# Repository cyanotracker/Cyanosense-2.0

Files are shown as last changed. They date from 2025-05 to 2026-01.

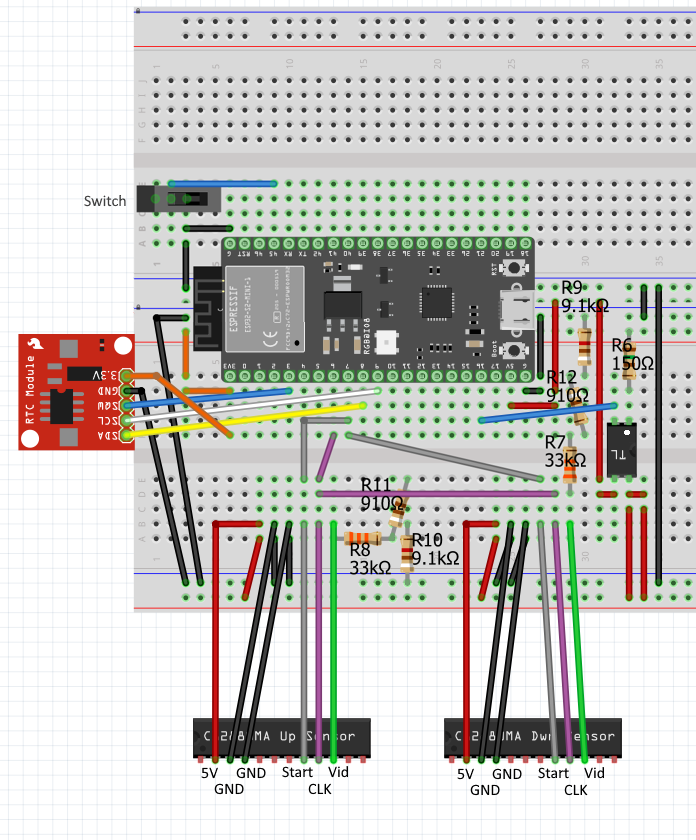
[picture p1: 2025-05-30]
Schematics/Fritizing Diagram Cyanosense 2.0 Offline Verison.png

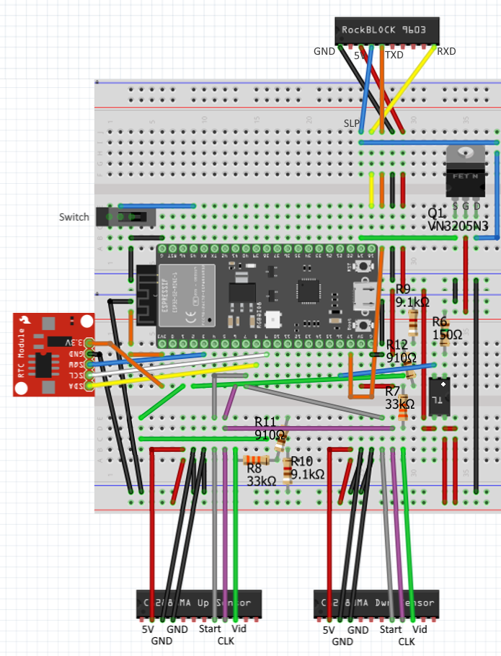
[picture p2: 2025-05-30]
Schematics/Fritizing Diagram Cyanosense 2.0 with Sat Modem.png

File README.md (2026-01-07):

# 🌊 CyanoSense 2.0 (CS2.0) – Low-Cost Hyperspectral System for CyanoHAB Monitoring






**CyanoSense 2.0 (CS2.0)** is a compact, low-cost, open-source spectroradiometer designed to support real-time and offline monitoring of **Cyanobacterial Harmful Algal Blooms (CyanoHABs)** in inland and coastal waters. This repository includes all components needed to **reproduce, assemble, and operate** the CS2.0 device.

> 🛰️ CS2.0 was developed as a complementary in situ validation tool for satellite-based CyanoHAB monitoring.  
> 📝 A scientific publication describing CS2.0 now published. Please cite the work appropriately (see [Citation section](#-citation)) and refer to the paper for broader scientific context and applications.

---

## 📦 What's in This Repository?

This repository includes:

1. 🧩 **3D Printed Parts** – STL files and models for the CS2.0 housing and optical mount components.  
2. 🛠️ **Mechanical Assembly Instructions** – Step-by-step guide with diagrams and instructions for assembling CS2.0.  
3. ⚡ **Electronic Schematics** – Circuit diagrams and wiring layout.  
4. 📷 **Prototype Pictures** – Reference images of a fully built and field-deployed CS2.0 unit.  
5. 💾 **Offline Data Download Instructions** – Guidelines for retrieving stored measurements from the device when internet is not available.  
6. 📂 **Documents Folder** – Contains the **Bill of Materials** (BOM) and **Hamamatsu documentation** including the wavelength space coefficients and sensor specifications.  
   - 📌 An **exhaustive list of all components used** in this project can be found in the Bill of Materials (`Documents/Bill of Materials`).  

🎥 A **tutorial video demonstrating the operation** of CS2.0 is also provided: https://youtu.be/9sZjeJtRidM

---

## 📡 Sensor Details

CS2.0 uses the **Hamamatsu C12880MA** mini-spectrometer to capture hyperspectral light spectra in the range of 380nm - 880nm.

- Records data in **6 channels**, each corresponding to a segment of the full sensor array.  
- Includes calibration code to convert raw intensity values into continuous **wavelength space** using a polynomial mapping.  
- Wavelength mapping is implemented using conversion coefficients provided in the Hamamatsu documentation (see `Documents/`) and handled in the included data extraction code (`/Code/`).  
- Real-time or offline data download is managed through the [CoolTerm](https://freeware.the-meiers.org/) serial terminal tool, described in `/Offline Mode (Download Data off Prototype)/`.

---

## 📚 Usage

To build a CS2.0 prototype and use it for yourself:
- Follow the mechanical and electrical instructions in the `/Mechanical Assembly Instructions/` and `/Schematics/` folders.
- Use `/offline_data/` for accessing data stored during field deployments without real-time upload.

### 🌐 Satellite Data Validation

CS2.0 can be used to **validate satellite-based CyanoHAB products**:
- Overlay CS2.0-derived in situ spectra with coincident satellite-derived reflectance (e.g., Sentinel-2, Landsat, PACE).
- Helps assess model accuracy and algorithm performance under real-world conditions.
- Supports efforts in operational satellite monitoring by offering ground-based reference measurements.

---

## 📄 Citation

- **This sensor and methodology are described in a scientific article, now published open access in *ACS Environmental Science and Technology, Water*.**  
- If you use or build on this work, **please cite the associated article as follows:**<br>
Maniyar, C.B.; Raviprakash, K.; Kumar, A; Seferian, M. A; Firotentino, I and Mishra, D. R. (2025) **Low-Cost System to Support and Expand Cyanobacterial Harmful Algal Bloom Monitoring with New-Generation Ocean Color Satellites.** *ACS Environmental Science and Technology, Water*. DOI: [10.1021/acsestwater.5c00301](https://doi.org/10.1021/acsestwater.5c00301)   
- The article provides a deeper understanding of how CS2.0 fits into the broader **CyanoHAB monitoring paradigm**, including its role in supporting satellite remote sensing efforts.

---

## 🪪 License

- **Code**: [MIT License](LICENSE)
- **Documentation, Schematics, and Hardware Designs**: [Creative Commons Attribution 4.0 International (CC BY 4.0)](https://creativecommons.org/licenses/by/4.0/)

---

## 📬 Contact

For questions, collaborations, or issues, please reach out to:  
**Chintan B. Maniyar** at
📧 [chintanmaniyar@uga.edu] OR [cyanotracker@gmail.com]

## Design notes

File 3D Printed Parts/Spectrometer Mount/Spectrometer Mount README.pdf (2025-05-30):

### Spectrometer Mount

- Allows Spectrometers to be mounted.
- Slips on the Electronics Housing four outer Posts. Requires the Electronics Housing to be modified by trimming the four outer posts by 0.15in (circled in red in Image 2).
- One Spectrometer Mount per sensor. Same mount works for both.
- The Spectrometer Mount should be printed using PETG or similar material

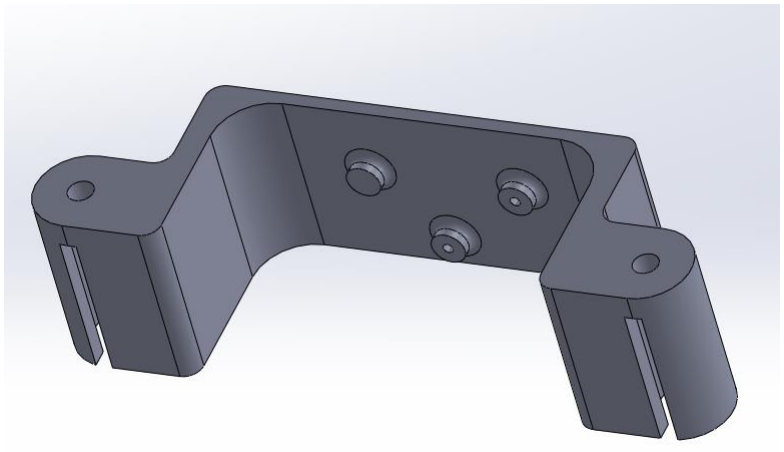
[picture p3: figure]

Image 1

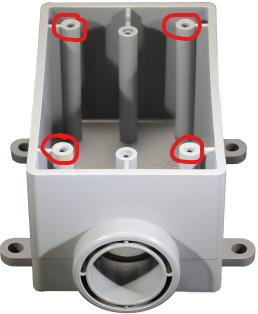
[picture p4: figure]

Image 2

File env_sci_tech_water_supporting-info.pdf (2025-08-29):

Low-cost System to Support CyanoHAB Monitoring with New Generation Ocean Color Satellites: Supporting Information

A GitHub repository containing all designs, schematics, bill of materials and documentation necessary to reproduce and replicate Cyanosense2.0 sensor can be found here: https://github.com/cyanotracker/Cyanosense-2.0

A video demonstrating operation of Cyanosense2.0 can be found here: https://youtu.be/9sZjeJtRidM

A. CyanoHAB Models and Indices; and Uncertainty Metrics

NDCI =

Rrs(708)−Rrs(665)
Rrs(708)+Rrs(665)

(1)

PC3 = (Rrs

−1
(620) − Rrs

−1
(665)) × Rrs(708) | (2)

CI = −1 × { Rrs(681) − Rrs(665) − (Rrs(708) − Rrs(665)) ×

681−665
708−665
} | (3)

PCI = Rrs(560) − Rrs(620) + (Rrs(665) − Rrs(560)) ×

620−560
665−560

(4)

where Rrs(560) and corresponds to OLCI's band-6; Rrs(620) corresponds to OLCI's band-7; Rrs(665) corresponds to OLCI's band-8; Rrs(681) corresponds to OLCI's band-10; Rrs(708) corresponds to OLCI's band-11. These bands are available on PACE OCI verbatim.

A.1 Uncertainty Metrics for Model Validation and Spectral Magnitude Evaluation

%NRMSE = √∑
(pi−pi

′
)

2
n

n
i=1 | ×

1

pmax−pmin

× 100% | (5)

MAPE =

1
n

∑

|pi−pi

′
pi

n
i=1 | × 100% | (6)

β = 100 × sgn (median (loge (
pi

′

pi

))) × (e

|median(loge(
pi

′

pi

))|
| | − 1) (7)

where p is the reference value (SVC-HR); p' is the measured value (CS2.0); n is the total number of samples.

A.2 Uncertainty Metrics for Spectral Shape Evaluation

SAM = cos

−1 (
RrsCS2.0⋅RrsSVC
||RrsCS2.0|| ||RrsSVC||
) | (8)

SID(p, q) = Σi pi

′
log(

pi

′

pi

) + pi

log(

pi

′

pi

) | (9)

SED = √∑ | (RrsCS2.0 − RrsSVC)
N | 2
i=1

(10)

where p is the reference value (SVC-HR); p' is the measured value (CS2.0); N is the total number of wavenumbers (wavelength).

B. Calibration Coefficients for Lw, Lc and Lsky

The Hamamatsu C12880MA spectrometer records data in a 6-channel pixel space, which is converted to wavelength space using coefficients provided by the manufacturer as found in this document. (https://github.com/cyanotracker/Cyanosense-2.0/blob/main/Documents/Sensor%20Calibration%20Data.pdf) Once in wavelength space, the data is still in Arbitrary Units (AU), representing Intensity. To convert this intensity into various radiances (Lw, Lc and Lsky); we provide a wavelength-dependent set of coefficients and biases below for each component for the wavelength range 390nm – 880nm. This table can be found at the end of this document due to its length. Figure 1 shows the Rrs spectra from CS2.0 overlaid with coincident Rrs spectra from SVC-HR, following leave-one location out cross-validation, for all stations across the 6 study sites (lakes).

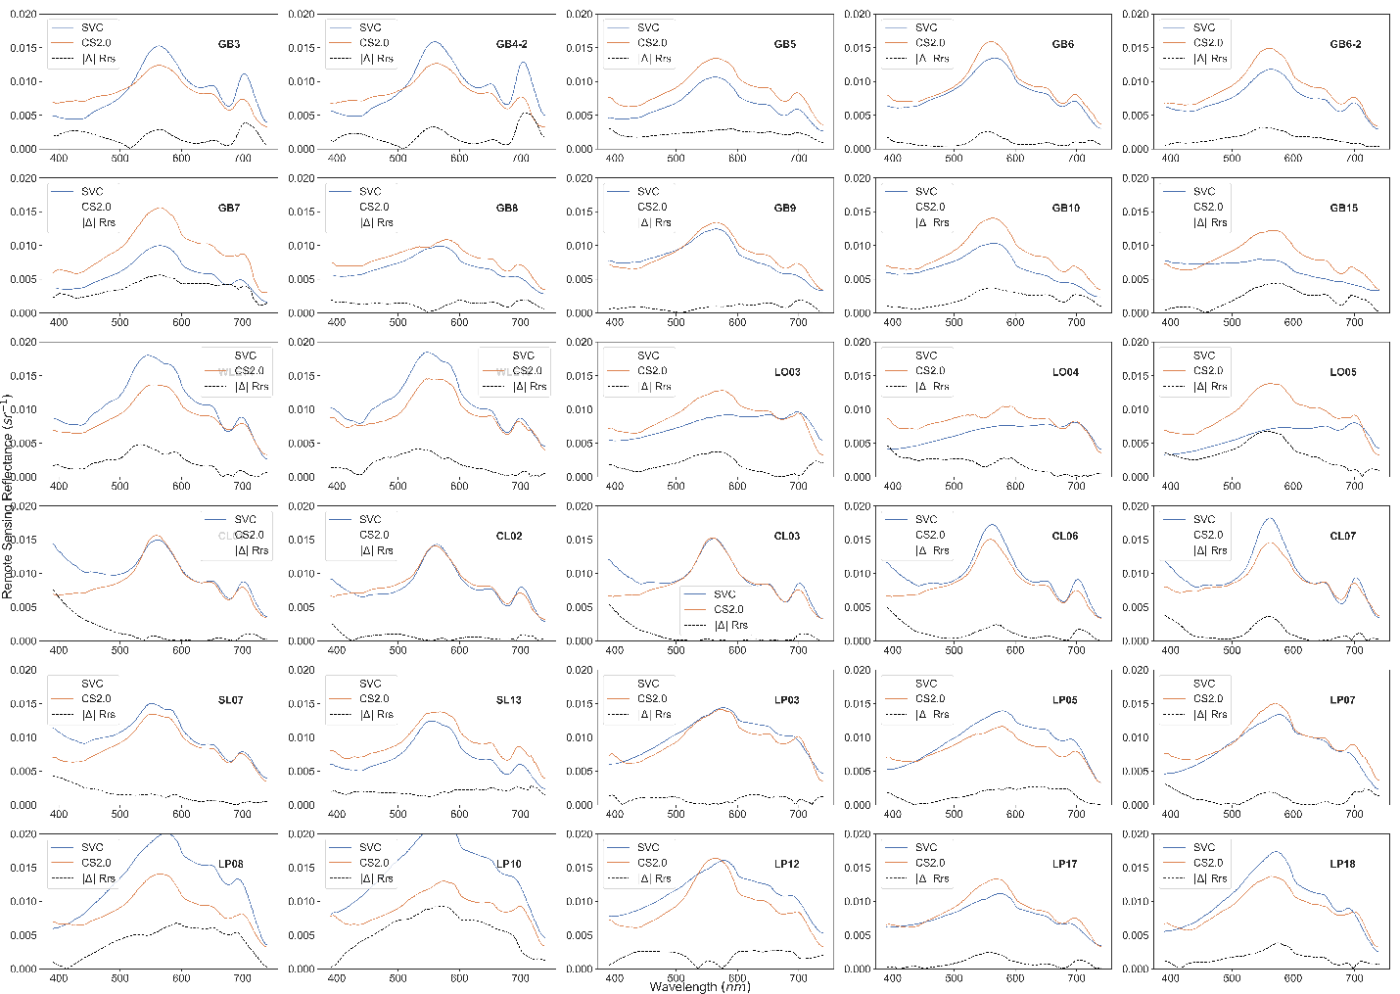
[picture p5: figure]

Figure 1: In-situ Rrs spectra of CS2.0 and SVC overlayed onto each other for all sampling stations. Dotted line represents absolute error in Rrs for CS2.0 spectra with SVC spectra as reference.

C. Upscaling CS2.0 to Satellite Spectral Configuration: Radiometric Evaluation

Table 1: A summary of evaluation metrics for - (Top half): CyanoHAB specific bands in PACE (OCI) as well as Sentinel-3 (OLCI). Satellite Rrs simulated from CS2.0 is evaluated against satellite Rrs simulated from SVC-HR; and (Bottom half): CyanoHAB indices/models applied on PACE (OCI) as well as Sentinel-3 (OLCI). Satellite indices/models simulated from CS2.0 are evaluated against the corresponding ones simulated from SVC-HR.

%NRMSE and MAPE | R
| | | | 2 | Band Usage
| PACE (OCI) | Sentinel-3 (OLCI) | PACE (OCI) | Sentinel-3 (OLCI)
CyanoHAB Specific Bands
560 nm | 23.98% & 22.97% | 24.00% & 22.80% | 0.45 | 0.34 | PCI
620 nm | 21.62% & 20.33% | 21.63% & 20.33% | 0.41 | 0.40 | PC3, PCI
665 nm | 20.73% & 19.39% | 20.88% & 19.51% | 0.55 | 0.51 | NDCI, PC3, CI, PCI
681 nm | 19.92% & 18.34% | 19.83% & 18.34% | 0.58 | 0.61 | CI
708 nm | 22.6% & 24.19% | 22.66% & 24.19% | 0.32 | 0.38 | NDCI, PC3, PCI
CyanoHAB Specific Spectral Indices/Models
NDCI | 16.24% | 16.86% | 0.77 | 0.74 | -
PC3 | 16.51% | 16.64% | 0.77 | 0.75 | -
CI | 13.96% | 14.28% | 0.83 | 0.83 | -
PCI | 15.17% | 18.28% | 0.83 | 0.79s | -

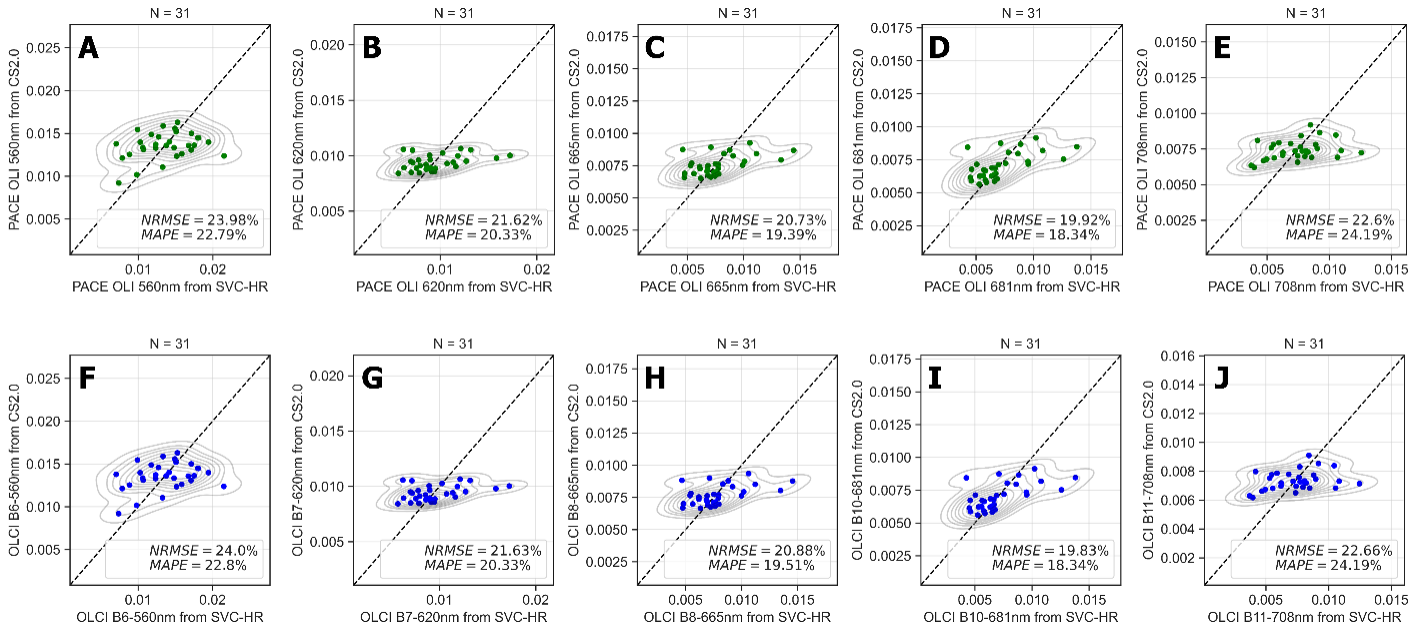
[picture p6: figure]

Figure 2: Top row (A-E): Validation of PACE {CS2.0} simulated Rrs with PACE {SVC-HR} simulated Rrs as reference (shown in green). Bottom row (F-J): Validation of OLCI {CS2.0} simulated Rrs with OLCI {SVC-HR} simulated Rrs as reference (shown in blue). Dotted line is the reference (1:1) line.

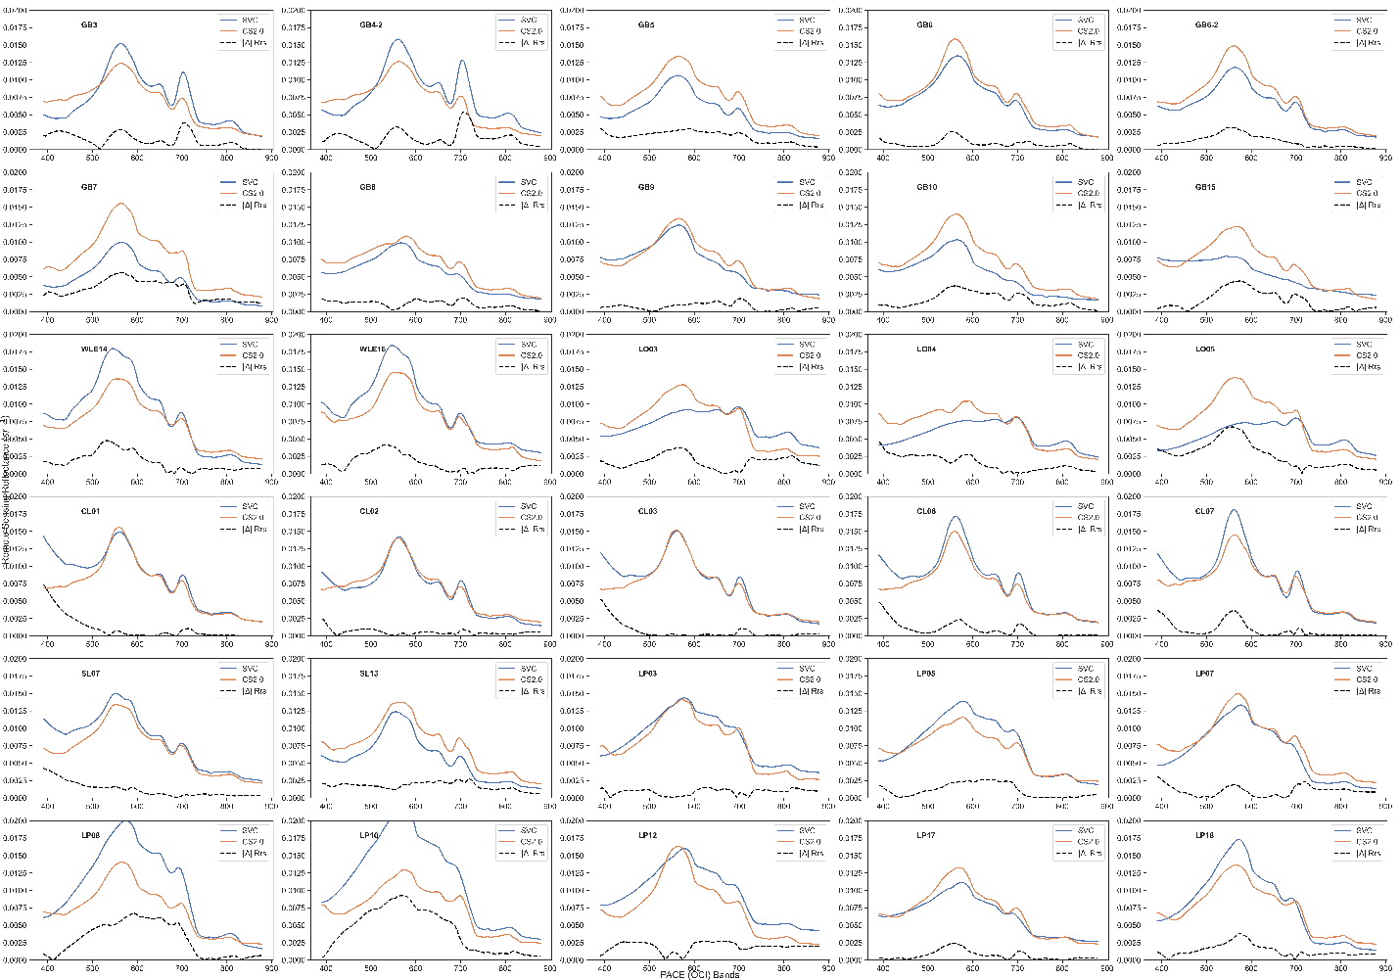
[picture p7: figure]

Figure 3: PACsE (OCI) spectral shape derived from PACECS2.0 Rrs (in orange) overlayed onto the corresponding spectral shape derived from PACESVC-HR Rrs (in blue) for all sampling stations. Dotted line is the relative error.

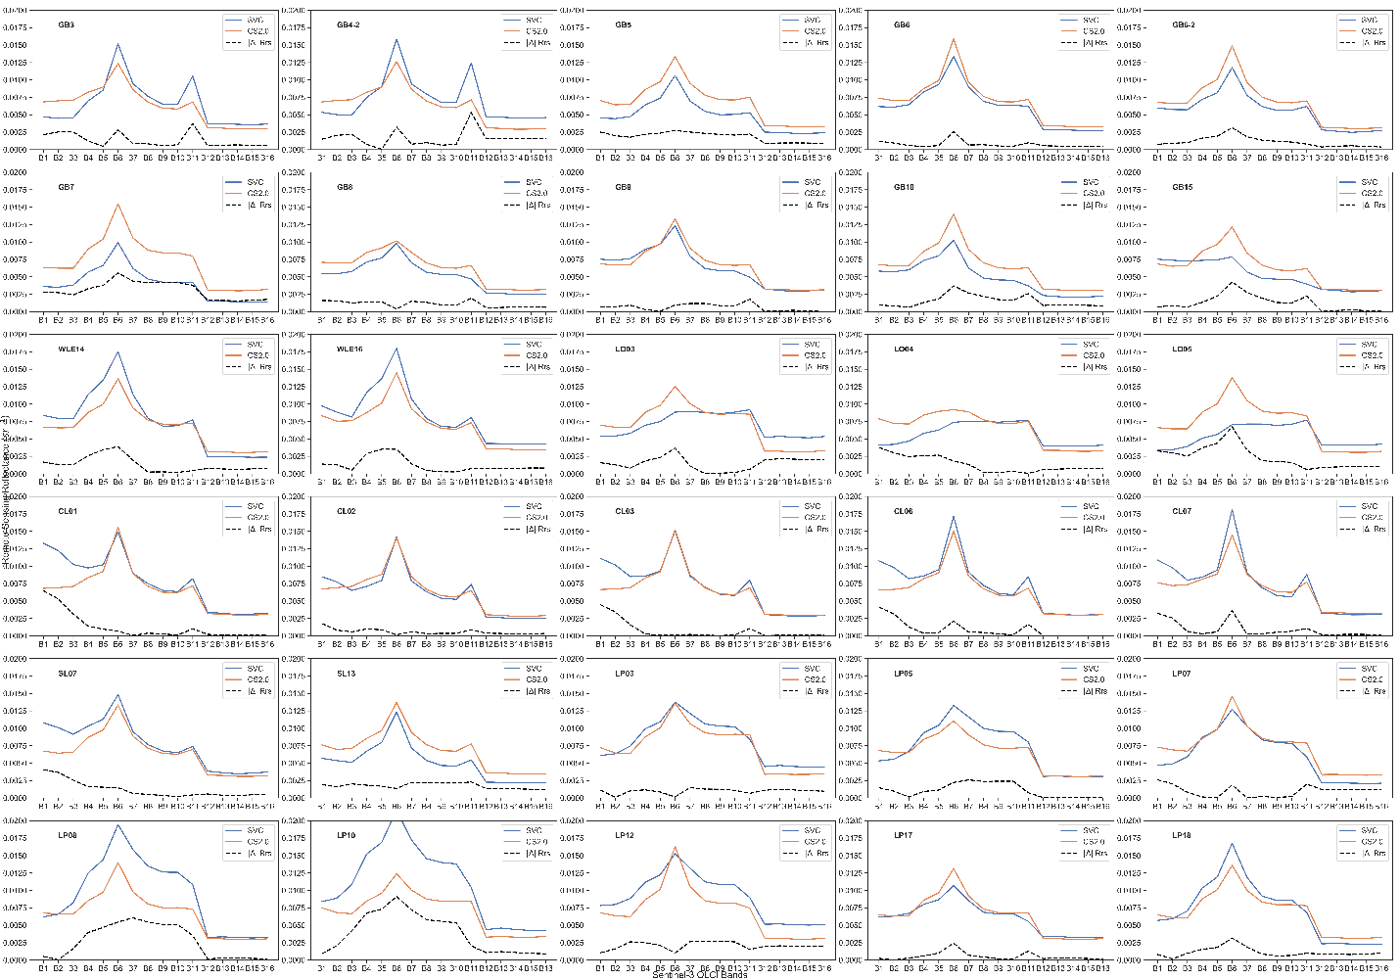
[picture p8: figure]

Figure 4: Sentinel-3 (OLCI) spectral shape derived from Sentinel-3CS2.0 Rrs (in orange) overlayed onto the corresponding spectral shape derived from Sentinel-3SVC-HR Rrs (in blue) for all sampling stations. Dotted line is the relative error.

D. List and Price of Components

Table 2 includes a comprehensive list of all the components used in the development of CS2.0, along with their price listings. This table also serves as a budget table for CS2.0. Each component name carries the hyperlink to its online listing that was used to make the purchase at the time of sensor development. Note that the prices are based on the EXACT number to build the prototype, unless noted otherwise. Tax and any shipping costs are NOT included. The total cost to build CS2.0 was $1,300.33.

Table 2: A comprehensive list of all components used in the development of CS2.0 with their price listings

Component | Quantity | Price | Purpose

Electronic Parts

Hamamatsu C12880MA Micro (https://www.digikey.com/en/products/detail/groupgets-llc/BO-HAMA-C12880-V2-SENSOR/14306449) | 2 ($350 each) | $700 | Spectrometers for CS2.0
Spectrometer (https://www.digikey.com/en/products/detail/groupgets-llc/BO-HAMA-C12880-V2-SENSOR/14306449)
TLP3556A Photorelay (https://www.mouser.com/ProductDetail/Toshiba/TLP3556ATP1F?qs=r5DSvlrkXmJCPc02EG%252Bwtw%3D%3D) | 1 | $4.20 | Turns sensors on and off
RockBlock 9603 Iridium (https://www.adafruit.com/product/4521) | 1 | $299.95 | Satellite data transmission for
Satellite Modem (https://www.adafruit.com/product/4521) | | | CS2.0
RockBlock 9603 Accessory (https://www.adafruit.com/product/4529) | 1 | $4.95 | Adapter cable to ESP32 interface
Cable (https://www.adafruit.com/product/4529)
M1600HCT-P-SMA Iridium (https://www.sparkfun.com/products/16838) | 1 | $64.95 | Antenna for Iridium modem
Passive Antenna (https://www.sparkfun.com/products/16838)
SMA Male with Waterproof (https://www.amazon.com/dp/B082964WZ3?psc=1&ref=ppx_yo2ov_dt_b_product_details) | 1 | $3.63 | Antenna cable for Iridium
Ring & Bulkhead Antenna with (https://www.amazon.com/dp/B082964WZ3?psc=1&ref=ppx_yo2ov_dt_b_product_details) | | | modem
Cable (https://www.amazon.com/dp/B082964WZ3?psc=1&ref=ppx_yo2ov_dt_b_product_details)
ESP32-S2 Saola Dev Kit (https://www.adafruit.com/product/4693) | 1 | $14.50 | Microcontroller for the system
DS3231 Real Time Clock (https://www.amazon.com/DS3231-Precision-AT24C32-Arduino-Raspberry/dp/B07V68443F/ref%3Dsr_1_1_sspa) | 1 | $3.80 | RTC to control wake-up and
| | | sleep for ESP32
DIYHZ 1P2T SPFT Vertical (https://www.amazon.com/dp/B07BD1SPYG?psc=1&ref=ppx_yo2ov_dt_b_product_details) | 1 | $0.09 | Slide switch to toggle ESP32
Slide Switch (https://www.amazon.com/dp/B07BD1SPYG?psc=1&ref=ppx_yo2ov_dt_b_product_details) | | | between manual and
| | | autonomous mode
Voltaic 2W Solar Charger Kit (https://voltaicsystems.com/2-watt-kit/) | 1 | $5.99 | Solar panel and battery
USB to Micro USB Cable (https://www.amazon.com/dp/B07CKXQ9NB?ref=ppx_yo2ov_dt_b_product_details&th=1) | 1 | $4.99 | Connects ESP32 to battery
SchmalzTech Breadboard (https://www.amazon.com/dp/B0B1XGCFGW?psc=1&ref=ppx_yo2ov_dt_b_product_details) | 2 ($8.99 each) | $17.98 | Breadboard for system
ST-BB-470 (https://www.amazon.com/dp/B0B1XGCFGW?psc=1&ref=ppx_yo2ov_dt_b_product_details)
Jumper Wire Kit (https://www.amazon.com/AUSTOR-Lengths-Assorted-Preformed-Breadboard/dp/B07CJYSL2T/ref%3Dsr_1_4) | 1 | $11.99 | Wiresfor breadboard
10 cm Jumper Wires Assorted (https://www.amazon.com/dp/B07GD1XFWV?ref=ppx_yo2ov_dt_b_product_details&th=1) | 1 | $6.98 | Jumper wires for RTC
Kit (https://www.amazon.com/dp/B07GD1XFWV?ref=ppx_yo2ov_dt_b_product_details&th=1)
40 cm Jumper Wires Assorted (https://www.amazon.com/dp/B07GD1TH2K?ref=ppx_yo2ov_dt_b_product_details&th=1) | 1 | $11.99 | Jumper wires for spectrometers
Kit (https://www.amazon.com/dp/B07GD1TH2K?ref=ppx_yo2ov_dt_b_product_details&th=1)

Mechanical Parts

Waterproof Electrical Junction (https://www.amazon.com/dp/B0B87VR84G?ref=ppx_yo2ov_dt_b_product_details&th=1) | 1 | $19.99 | Electronics housing
Box IP67 (https://www.amazon.com/dp/B0B87VR84G?ref=ppx_yo2ov_dt_b_product_details&th=1)
PVC 1-Gang Type FSE Box (https://www.lowes.com/pd/Kraloy-PVC-3-4-in-FSE-Single-Gang-Box-91-Hub-93/5001212811) | 1 | $7.68 | Sensor housing
TayMac 1-Gang Weatherproof (https://www.lowes.com/pd/TayMac-1-Gang-Rectangle-Plastic-Weatherproof-Electrical-Box-Cover/5004945479) | 1 | $3.58 | Cover for sensor housing
Box Cover (https://www.lowes.com/pd/TayMac-1-Gang-Rectangle-Plastic-Weatherproof-Electrical-Box-Cover/5004945479)
10 ft Schedule 40 PVC Conduit (https://www.lowes.com/pd/CANTEX-Common-3-4-in-Actual-75-In-Non-Metallic-Pvc-10-ft-Conduit/3568512) | 1 | $2.06 | To connect sensor and electronic
| | | housings. Cut to 2 ft.
Schedule 40 PVC Bushing (https://www.lowes.com/pd/CANTEX-3-4-in-Bushing-Connector-Schedule-40-PVC-Compatible-Schedule-80-PVC-Compatible-Conduit-Fitting/1000321591) | 1 | $0.60 | Attaches PVC pipe to electronics
Connector Conduit Fitting (https://www.lowes.com/pd/CANTEX-3-4-in-Bushing-Connector-Schedule-40-PVC-Compatible-Schedule-80-PVC-Compatible-Conduit-Fitting/1000321591) | | | housing
3/4-in Zinc-plated Steel Conduit (https://www.lowes.com/pd/Sigma-Electric-ProConnex-3-4-in-Conduit-Locknut-Intermediate-Metal-Conduit-Compatible-Galvanized-Rigid-Conduit-Compatible-Rigid-Metal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) | 1 | $0.39 | Screws the bushing connector to
Locknut (https://www.lowes.com/pd/Sigma-Electric-ProConnex-3-4-in-Conduit-Locknut-Intermediate-Metal-Conduit-Compatible-Galvanized-Rigid-Conduit-Compatible-Rigid-Metal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) | | | the electronics housing

1-in Zinc-plated Standard Flat (https://www.lowes.com/pd/Hillman-1-Count-x-2-in-Zinc-Plated-Standard-SAE-Flat-Washer/3006230) | 1 | $0.78 | Adds support to the inside of the
Washer (https://www.lowes.com/pd/Hillman-1-Count-x-2-in-Zinc-Plated-Standard-SAE-Flat-Washer/3006230) | electronics housing to prevent
flex
1/2-inch Oversize Union Washer (https://www.amazon.com/dp/B09TPGN29W?psc=1&ref=ppx_yo2ov_dt_b_product_details) | 1 | $0.30 | Waterproofs the electronics box
Flat Plumbing Slip Joint Washer (https://www.amazon.com/dp/B09TPGN29W?psc=1&ref=ppx_yo2ov_dt_b_product_details) | to pipe connection
Rubber (https://www.amazon.com/dp/B09TPGN29W?psc=1&ref=ppx_yo2ov_dt_b_product_details)
3x30mm Round Aluminum (https://www.amazon.com/dp/B01MYBB70W?ref=ppx_yo2ov_dt_b_product_details&th=1) | 4 | $4.60 | Standoff to support top layer in
Column Standoffs (https://www.amazon.com/dp/B01MYBB70W?ref=ppx_yo2ov_dt_b_product_details&th=1) | electronics box
3x16mm Thumb Screws (https://www.amazon.com/dp/B01MSLME5A?psc=1&ref=ppx_yo2ov_dt_b_product_details) | 4 | $5.20 | To screw down top layer
4/40 Hex Machine Nuts (https://www.amazon.com/Hillman-140009-Machine-Screw-Piece/dp/B001B2QP3C/ref%3Dsr_1_3?s=industrial) | 4 | $0.24 | Nuts to screw solar panel
M3x Screws (https://www.amazon.com/uxcell-M3x10mm-Phillips-Stainless-Fasteners/dp/B07MF2ZTBG/ref%3Dsxin_16_pa_sp_search_thematic_sspa?cv_ct_cx=m3x10%2Bmachine%2Bscrews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) | 4 | $0.94 | Screws standoffs to mounting
plate in electronics housing
Microscope Cover Glass Slips (https://www.amazon.com/dp/B095N8DNY1?psc=1&ref=ppx_yo2ov_dt_b_product_details) | 2 | $8.99 (not | Cover glass were used as the
exact) | lens for spectrometer housing
GE Advanced Silicone (https://www.amazon.com/GE-GE500-Silicone-Window-Squeeze/dp/B000M2UPAG/ref%3Dsr_1_17) | 1 | $14.99 (not | To seal solar panel and cable for
exact) | waterproofing; to attach glass
lens in sensor housing
Miscellaneous* | 1 | $20 (not | TPU material used for 3D
exact) | printed FOV adapter, PETG
material, other 3D printed parts and foam pads used for battery
Total Cost | $1,300.33

*Gray card (external to the CS2.0 system) for radiometric calibration of the spectrometer can be obtained at a nominal price of $5: https://a.co/d/i3NDbEW

E. Heatproof Testing on Field

To test the heatproof design of the sensor and electronics housing, CS2.0 was deployed in autonomous mode for a week at Lake Herrick in Athens, Georgia. Ambient temperature and temperature inside the electronics and sensor housing box was recorded every half an hour. Tables 3 and 4 show the temperature variation from the most sunny and the most cloudy days of the week.

Table 3: Temperature Data from 3/31/23 (Red Textshows highest Box Temp)

Time | Box ◦C | Ambient ◦C | Outside Conditions
10:30 am | 24.0 | 18.9 | Cloudy
11:00 am | 25.2 | 19.5 | Cloudy
11:30 am | 26.9 | 20.9 | Cloudy
12:00 pm | 29.8 | 22.2 | Partially Sunny
12:30 pm | 31.5 | 23.0 | Partially Sunny
01:00 pm | 32.6 | 23.7 | Partially Sunny
01:30 pm | 30.1 | 24.4 | Cloudy
02:00 pm | 31.5 | 24.6 | Partially Sunny
02:30 pm | 32.1 | 24.8 | Partially Sunny
03:00 pm | 28.9 | 24.3 | Cloudy
03:30 pm | 26.4 | 24.0 | Cloudy
04:00 pm | 32.1 | 23.9 | Partially Sunny
04:30 pm | 27.1 | 23.5 | Cloudy
05:00 pm | 31.5 | 23.2 | Partially Sunny
05:30 pm | 29.0 | 23.0 | Cloudy
06:00 pm | 27.0 | 22.7 | Cloudy

Table 4: Temperature Data from 4/1/23 (Red Text shows highest Box Temp)

Time | Box ◦C | Ambient ◦C | Outside Conditions
01:00 pm | 36.3 | 22.2 | Sunny
01:30 pm | 38.6 | 22.9 | Sunny
02:00 pm | 39.4 | 25.4 | Sunny
02:30 pm | 38.8 | 26.3 | Sunny
03:00 pm | 39.1 | 26.2 | Sunny
03:30 pm | 39.3 | 26.5 | Sunny
04:00 pm | 39.2 | 26.8 | Sunny
04:30 pm | 38.3 | 26.6 | Sunny
05:00 pm | 33.3 | 25.0 | Sunny
05:30 pm | 29.0 | 23.0 | Cloudy
06:00 pm | 27.0 | 22.7 | Cloudy
F. Power Budget from Field Operation

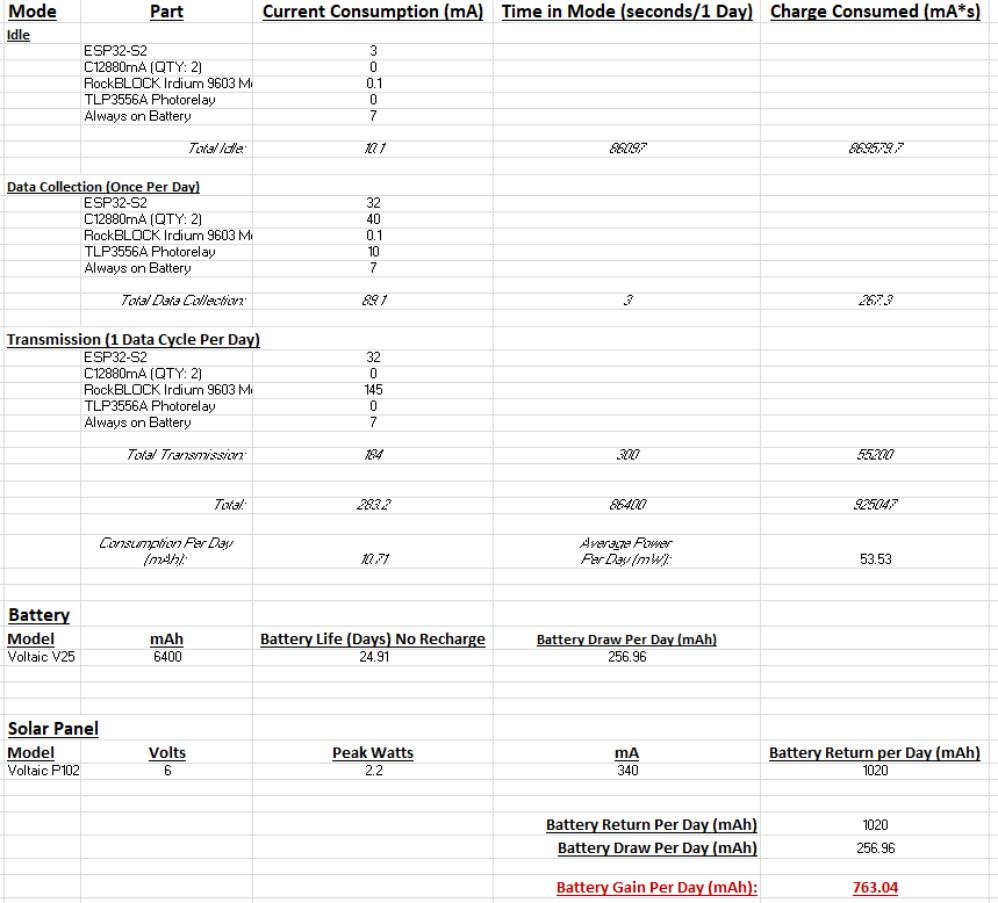
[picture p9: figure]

Figure 2: Actual power budget recorded after field-deployment of CS2.0

Table 2: Calibration coefficients to convert CS2.0 AU to Radiance (390nm – 880nm)

Wavelength | Lw | Lc | Lsky
Coefficient | Bias | Coefficient | Bias | Coefficient | Bias
390 | -0.377420664 | 6232.905 | 13.05778056 | 116470 | 3.007927386 | 43970.94
391 | -0.31822665 | 5671.419 | 11.58347595 | 107223.1 | 2.659524231 | 40136.66
392 | -0.283673801 | 5447.732 | 10.97939188 | 104127.6 | 2.527039034 | 38673.75
393 | -0.252053223 | 5228.914 | 10.40399777 | 101064.3 | 2.399893116 | 37209.26
394 | -0.20133233 | 5080.749 | 9.820725814 | 100274.6 | 2.224268735 | 36576.97
395 | -0.171353458 | 5196.92 | 9.739188789 | 104370.7 | 2.189416713 | 37962.29
396 | -0.164189121 | 5373.281 | 9.858000178 | 108557.6 | 2.232114083 | 39152.24
397 | -0.166732543 | 5999.62 | 10.81811365 | 123296.9 | 2.465840795 | 43535.29
398 | -0.169384947 | 6590.819 | 11.48004436 | 137701 | 2.658099038 | 47812.75
399 | -0.181796642 | 7227.734 | 12.10525959 | 152174.5 | 2.873149956 | 51749.96
400 | -0.192090515 | 8036.909 | 12.4003705 | 175655.9 | 3.131415331 | 56862.43
401 | -0.222795853 | 8283.76 | 12.41530014 | 179658.6 | 3.197529273 | 57193.25
402 | -0.251521545 | 8526.865 | 12.30716215 | 184576.2 | 3.260941638 | 57527.1
403 | -0.269243666 | 8608.086 | 11.88870645 | 187942.1 | 3.262473675 | 56635.39
404 | -0.286053748 | 8617.279 | 11.66481333 | 187241.1 | 3.245135617 | 55592.96
405 | -0.300460512 | 8618.181 | 11.36599549 | 187125.8 | 3.225967583 | 54561.39
406 | -0.306311257 | 8623.513 | 11.14471053 | 189422.6 | 3.242026289 | 53529.41
407 | -0.318471205 | 8795.883 | 11.11447854 | 194319.4 | 3.322266214 | 53170.01
408 | -0.334832259 | 8948.358 | 10.70657061 | 199365 | 3.378428783 | 52764.01
409 | -0.353354029 | 9094.713 | 10.53986723 | 202886.8 | 3.447308776 | 52466.27
410 | -0.363952303 | 9312.512 | 10.37199412 | 210647.1 | 3.555777653 | 52619.75
411 | -0.380574994 | 9509.185 | 10.07485453 | 217455.6 | 3.645712163 | 52696.69
412 | -0.411278136 | 9767.2 | 9.564034891 | 226160.6 | 3.744305954 | 52785.21
413 | -0.42896204 | 9928.667 | 8.764538428 | 236511.5 | 3.822303668 | 52355.29
414 | -0.448300993 | 10035.2 | 8.616180935 | 238928.4 | 3.86887533 | 51966.55
415 | -0.466471134 | 10136.64 | 8.460274949 | 241408.4 | 3.915055861 | 51580.45
416 | -0.470185205 | 10110.08 | 8.235706463 | 242072.7 | 3.922329896 | 50492.66
417 | -0.486716481 | 10134.48 | 8.071849322 | 241899.8 | 3.924576815 | 49881.57
418 | -0.502227969 | 10153.58 | 7.91077645 | 241703.4 | 3.925525397 | 49277.58
419 | -0.510918898 | 10225.86 | 7.894340963 | 244660.1 | 3.974104264 | 48862
420 | -0.537795881 | 10326.13 | 7.980960953 | 244842.3 | 4.029193663 | 48530.23
421 | -0.563588116 | 10419.35 | 8.050386137 | 245160.7 | 4.081113403 | 48222.09
422 | -0.572163781 | 10410.38 | 8.314467521 | 243910.7 | 4.103872234 | 47588.02
423 | -0.577193174 | 10324.52 | 8.460137732 | 239919.9 | 4.078685852 | 46587.9
424 | -0.599367043 | 10393.12 | 8.594059284 | 238817.6 | 4.091664849 | 46433.58
425 | -0.626876918 | 10466.84 | 8.98596203 | 235843.4 | 4.082342477 | 46544.27
426 | -0.631175062 | 10332.04 | 9.163530475 | 230655.8 | 4.000051568 | 45761.32
427 | -0.619617344 | 10081.7 | 9.005153828 | 224372.8 | 3.894867082 | 44460.92
428 | -0.606648042 | 9825.928 | 8.835191946 | 218178.2 | 3.788672614 | 43158.21

429 | -0.561038858 | 9215.235 | 8.506050111 | 205399.7 | 3.590927477 | 40237.13
430 | -0.570113136 | 9304.418 | 8.702257652 | 207105.9 | 3.659329187 | 40289.07
431 | -0.578240853 | 9389.436 | 8.898709286 | 208813.3 | 3.727699605 | 40346.45
432 | -0.587022747 | 9966.783 | 9.569912015 | 225863 | 4.033819808 | 42754.19
433 | -0.59099272 | 10197.47 | 9.730694667 | 232794.4 | 4.122820593 | 43682.35
434 | -0.594764439 | 10427.5 | 9.876147436 | 239839.5 | 4.211336079 | 44611.27
435 | -0.589153659 | 10685.71 | 10.04438109 | 249348 | 4.343050994 | 45501.61
436 | -0.571118906 | 10709.44 | 9.894504736 | 253717.8 | 4.386117311 | 45280.43
437 | -0.557233199 | 10609.4 | 9.771882112 | 252965.8 | 4.372413169 | 44725.45
438 | -0.542923125 | 10507.64 | 9.647375746 | 252227.2 | 4.358105065 | 44172.77
439 | -0.522400982 | 10510.58 | 9.788509669 | 255020.1 | 4.409910718 | 43943.34
440 | -0.521749439 | 10712.29 | 10.01203249 | 260974.7 | 4.492541929 | 44637.78
441 | -0.520927516 | 10913.26 | 10.23126292 | 266958.7 | 4.574952564 | 45333.07
442 | -0.51949674 | 11266.2 | 10.58432657 | 277186.3 | 4.718470005 | 46382.61
443 | -0.504414425 | 11280.27 | 10.20394428 | 281081.2 | 4.749829451 | 45985.33
444 | -0.488855282 | 11290.68 | 9.729485186 | 285712.5 | 4.78017559 | 45591.19
445 | -0.478545415 | 11368.66 | 9.70159223 | 288072.4 | 4.810839507 | 45212.83
446 | -0.4740744 | 11567.84 | 9.765876819 | 293293 | 4.891614618 | 45240.53
447 | -0.474438534 | 11779.02 | 9.848005054 | 299231.4 | 4.988401611 | 45669.76
448 | -0.471310601 | 11984.28 | 10.11585203 | 303570 | 5.058368711 | 46181.09
449 | -0.473061576 | 12343.07 | 10.38235522 | 311328.8 | 5.156335673 | 46811.51
450 | -0.465405798 | 12363.08 | 10.26797501 | 312393.1 | 5.164262001 | 46468.2
451 | -0.457252401 | 12380.52 | 10.14650531 | 313514.1 | 5.171954069 | 46125.97
452 | -0.440936068 | 12230.3 | 9.834662824 | 309820.6 | 5.086057474 | 44737.08
453 | -0.425942747 | 12167.74 | 9.700054265 | 309697.4 | 5.071925859 | 44301.09
454 | -0.410470641 | 12102.57 | 9.555039623 | 309656.1 | 5.057244874 | 43867.17
455 | -0.401351345 | 12327.04 | 9.623289802 | 316461.5 | 5.126780786 | 44003.66
456 | -0.385781828 | 12421 | 9.516204039 | 320779.7 | 5.145006571 | 43770.67
457 | -0.370448274 | 12381.98 | 9.312389063 | 321981.8 | 5.126986026 | 43388.25
458 | -0.355924119 | 12342.27 | 8.405580509 | 328947.4 | 5.137472448 | 42960.52
459 | -0.333581403 | 12343.01 | 7.457138923 | 338435.7 | 5.166304464 | 42460.62
460 | -0.321370479 | 12385.49 | 7.463701484 | 340866.3 | 5.177313335 | 42446.02
461 | -0.309182285 | 12427.37 | 7.457393277 | 343398.4 | 5.187963512 | 42432.9
462 | -0.286745006 | 12414.32 | 7.32763906 | 345810.5 | 5.169054216 | 42062.86
463 | -0.264907712 | 12291.53 | 7.251180198 | 344374.4 | 5.156636772 | 41308.19
464 | -0.242968012 | 12165.56 | 7.136884076 | 343240.3 | 5.142706396 | 40561.36
465 | -0.20987202 | 11905.74 | 7.018596703 | 339121.3 | 5.057779797 | 39364.72
466 | -0.181193955 | 11814.91 | 6.97083856 | 339549.6 | 5.033344198 | 38748.23
467 | -0.163442148 | 11742.6 | 6.824896759 | 339959.3 | 5.011830765 | 38387.17
468 | -0.140803081 | 11646.7 | 7.344805372 | 334995.3 | 4.998361506 | 37959.97
469 | -0.107590211 | 11572.15 | 7.92239053 | 331292.3 | 4.998059578 | 37449.57
470 | -0.084087516 | 11517.89 | 7.43942168 | 336310.2 | 5.015254389 | 37099.19
471 | -0.060640716 | 11461.33 | 6.824216369 | 342389.4 | 5.031304863 | 36753.31

472 | -0.0228028 | 11491.04 | 6.091305265 | 354531.4 | 5.091619996 | 36636.79
473 | 0.006325624 | 11377.26 | 6.404839267 | 352469.3 | 5.079065431 | 36294.27
474 | 0.0345321 | 11264.13 | 6.697515886 | 350561 | 5.064285541 | 35963.63
475 | 0.076608948 | 11101.56 | 5.699205033 | 359807.2 | 5.073742596 | 35308.75
476 | 0.120821996 | 10951.89 | 4.638147091 | 370443.4 | 5.106740199 | 34704.59
477 | 0.14685629 | 10891.21 | 3.494225006 | 381856.8 | 5.157457286 | 34425.86
478 | 0.166992877 | 10865.06 | 3.508715726 | 383930.9 | 5.193029803 | 34364.77
479 | 0.202498785 | 10802.74 | 3.387744969 | 387452.3 | 5.234968415 | 34160.77
480 | 0.224811677 | 10722.66 | 2.91331937 | 391760.7 | 5.243884077 | 34017.85
481 | 0.247264153 | 10641.49 | 2.434882702 | 396099.3 | 5.25265415 | 33875.82
482 | 0.281310916 | 10413.83 | 1.750260883 | 398328.8 | 5.198504097 | 33238.26
483 | 0.296318261 | 9932.445 | 1.238442726 | 386430.9 | 4.978863106 | 31706.02
484 | 0.303626211 | 9679.36 | 1.199278887 | 378508.5 | 4.871900901 | 30924.85
485 | 0.310483961 | 9423.961 | 2.061821542 | 363316.3 | 4.761384527 | 30100.72
486 | 0.326085331 | 9243.837 | 3.19144789 | 349661.6 | 4.69514689 | 29256.95
487 | 0.345323408 | 9344.968 | 2.523732382 | 361599.9 | 4.759563082 | 29574.61
488 | 0.364924721 | 9443.717 | 1.817634055 | 373838.6 | 4.823515938 | 29895.65
489 | 0.387452663 | 9581.807 | 0.678423501 | 390109.5 | 4.881568631 | 30107.83
490 | 0.399593228 | 9573.48 | 2.4121938 | 376687.1 | 4.894638663 | 29601.32
491 | 0.406058562 | 9559.578 | 4.33622045 | 361383.6 | 4.913089124 | 29254.48
492 | 0.422102663 | 9517.192 | 3.898860166 | 365229.1 | 4.911913489 | 29224.38
493 | 0.444286643 | 9599.35 | 3.548116795 | 372670.4 | 4.950969055 | 29335.84
494 | 0.462695101 | 9590.689 | 3.083261929 | 378245.4 | 4.962526336 | 29457.35
495 | 0.487639214 | 9545.159 | 1.982908827 | 388951.6 | 4.980634011 | 29570.57
496 | 0.506581422 | 9470.384 | 0.871690948 | 396188.6 | 4.943341397 | 29270.77
497 | 0.520091023 | 9391.494 | 0.909558726 | 393993.9 | 4.902396749 | 29201.71
498 | 0.534151127 | 9310.239 | 0.939182139 | 391866 | 4.860497239 | 29133.79
499 | 0.541415695 | 9202.687 | 1.038695418 | 385746.9 | 4.759547147 | 28687.99
500 | 0.561407503 | 9091.936 | 1.264532203 | 380660.7 | 4.649871362 | 28565.08
501 | 0.59073099 | 8995.64 | 1.500798416 | 378976.9 | 4.599094298 | 28826.42
502 | 0.609809094 | 8943.153 | 1.732874357 | 377321.7 | 4.568662511 | 28851.54
503 | 0.639145485 | 9052.038 | 1.94775519 | 381297.1 | 4.584773751 | 29156.23
504 | 0.672826777 | 8983.497 | 2.046391426 | 382554.2 | 4.603051281 | 29256.41
505 | 0.716914931 | 8871.242 | 2.341483544 | 382249.7 | 4.625394363 | 29463.83
506 | 0.768450706 | 8787.385 | 2.546938065 | 383148.3 | 4.659480213 | 29490.97
507 | 0.81161386 | 8683.309 | 3.501191505 | 375363.3 | 4.698484792 | 29231.03
508 | 0.858555075 | 8574.38 | 4.274737332 | 370790.3 | 4.756700755 | 29318.32
509 | 0.894503379 | 8522.242 | 4.607272561 | 369752.1 | 4.801373154 | 29398.57
510 | 0.934355743 | 8491.387 | 4.78717513 | 369000.4 | 4.838885001 | 29311.02
511 | 0.965416311 | 8391.752 | 4.956806642 | 366556.6 | 4.84314433 | 29264.88
512 | 1.028313484 | 8159.011 | 5.30977401 | 362755.1 | 4.901098016 | 29156.69
513 | 1.08782087 | 7873.258 | 5.44359426 | 356262.5 | 4.894266847 | 28640.26
514 | 1.105477981 | 7558.428 | 5.716809989 | 343145.6 | 4.775013813 | 27638.18

515 | 1.13400623 | 7318.749 | 6.079371063 | 335269.8 | 4.732612145 | 27163.1
516 | 1.163167526 | 7076.118 | 6.398602169 | 327735.5 | 4.689612548 | 26688.43
517 | 1.243585779 | 6778.348 | 6.582445157 | 325615.8 | 4.688048902 | 26385.91
518 | 1.345912107 | 6514.395 | 6.819358343 | 329297.6 | 4.765893193 | 26670.28
519 | 1.435319642 | 6261.497 | 6.715855534 | 335549.2 | 4.807224446 | 26966.42
520 | 1.538752748 | 6134.963 | 6.596439842 | 345698 | 4.880558642 | 27378.93
521 | 1.612462805 | 6057.544 | 6.674854833 | 351075.1 | 4.92335125 | 27475.01
522 | 1.667189485 | 5836.344 | 6.692514482 | 352003.2 | 4.917310248 | 27415.03
523 | 1.723524666 | 5603.051 | 6.709643158 | 352935.3 | 4.911227461 | 27355.27
524 | 1.776345225 | 5236.417 | 6.222701321 | 352634.1 | 4.8117601 | 26940.88
525 | 1.845250212 | 4786.314 | 5.785045631 | 354475.1 | 4.758290233 | 26791.76
526 | 1.923165914 | 4308.963 | 5.518612315 | 355039 | 4.741480185 | 26529.82
527 | 2.013407554 | 4075.983 | 5.385699512 | 360705.2 | 4.786341638 | 26546.68
528 | 2.090005936 | 4128.909 | 5.582902695 | 369058.1 | 4.86009208 | 27017.21
529 | 2.134360833 | 3907.558 | 5.641160228 | 369080.2 | 4.835108604 | 26989.32
530 | 2.179512359 | 3677.91 | 5.696349273 | 369125 | 4.8102764 | 26961.26
531 | 2.226649618 | 3417.387 | 5.70994434 | 365959.1 | 4.752289198 | 26657.57
532 | 2.317453051 | 2930.463 | 5.408945712 | 368256.9 | 4.75953583 | 26569.83
533 | 2.378103378 | 2642.504 | 5.512440857 | 367327.8 | 4.764653515 | 26442.88
534 | 2.474321999 | 2353.017 | 5.058879911 | 373762.8 | 4.825484123 | 26277.21
535 | 2.543317505 | 2131.993 | 5.020003641 | 374888.7 | 4.83825812 | 26065.15
536 | 2.644161578 | 1558.024 | 4.844611057 | 374629.3 | 4.816544097 | 25938.46
537 | 2.741960863 | 999.7602 | 4.670722273 | 374354.8 | 4.794489527 | 25812.02
538 | 2.79454347 | 581.0849 | 4.547480079 | 370844.8 | 4.714056832 | 25348.65
539 | 2.852567872 | 136.7766 | 4.505480326 | 369389.5 | 4.675762403 | 25151.64
540 | 2.898274719 | -118.227 | 4.719176434 | 365940.6 | 4.653295555 | 24937.37
541 | 2.969540751 | -355.254 | 5.00258842 | 364163.4 | 4.648504731 | 24731.95
542 | 3.070338515 | -630.641 | 5.254752424 | 365827.7 | 4.689557599 | 24733.43
543 | 3.132030717 | -892.683 | 5.342540462 | 366584.5 | 4.695803266 | 24825.28
544 | 3.188960516 | -1128.4 | 5.431283472 | 367334.5 | 4.701925032 | 24917.82
545 | 3.249348974 | -1384.45 | 5.457154093 | 367421.1 | 4.708061695 | 24737.18
546 | 3.295569106 | -1617.07 | 5.540596949 | 366034.4 | 4.702153029 | 24493.76
547 | 3.341819485 | -1872.14 | 5.29750825 | 367911.5 | 4.721238918 | 24307.62
548 | 3.386784061 | -2120.55 | 5.055634152 | 369775 | 4.740364026 | 24121.51
549 | 3.420802673 | -2134.36 | 5.188698846 | 369299.7 | 4.739897331 | 24006.54
550 | 3.431808409 | -2080.99 | 5.281424157 | 368661.8 | 4.745262427 | 23962.68
551 | 3.442952045 | -2027.95 | 5.365986553 | 368089.2 | 4.750556183 | 23919.36
552 | 3.478898694 | -2135.44 | 5.329259745 | 368929.6 | 4.771079795 | 23603.31
553 | 3.503487409 | -2192.07 | 5.324037436 | 369230.3 | 4.789498047 | 23284.8
554 | 3.494392461 | -2004 | 5.789458003 | 364866 | 4.807279547 | 23159.85
555 | 3.484994029 | -1814.88 | 6.207407913 | 360880.7 | 4.825071754 | 23036
556 | 3.438959308 | -1650.58 | 6.339471418 | 355228.9 | 4.779349601 | 22566.17
557 | 3.402621494 | -1474.06 | 6.552041104 | 351475.4 | 4.766770541 | 22351.58

558 | 3.366792687 | -1301.11 | 6.74935095 | 347839.3 | 4.754060924 | 22137.11
559 | 3.340800089 | -1068.58 | 6.874995903 | 345377.9 | 4.762472989 | 21826.55
560 | 3.336897685 | -837.594 | 7.072798458 | 345290.9 | 4.797772299 | 21698.05
561 | 3.336207696 | -645.177 | 7.537037711 | 342558.6 | 4.825384809 | 21694.39
562 | 3.334627101 | -447.85 | 7.967191725 | 340099.5 | 4.853075763 | 21692.07
563 | 3.327857643 | -263.863 | 8.192534821 | 338879.1 | 4.873303124 | 21509.52
564 | 3.305097142 | -62.8356 | 8.415260343 | 336451.8 | 4.870148926 | 21273.41
565 | 3.284272287 | 120.7501 | 8.619922527 | 334287.3 | 4.870663485 | 21151.75
566 | 3.271408045 | 281.1079 | 9.096940005 | 330010.4 | 4.863496211 | 21050.97
567 | 3.244206503 | 432.6905 | 9.534094352 | 324612.1 | 4.799973229 | 20829.13
568 | 3.204705546 | 736.5909 | 9.886859293 | 320966.1 | 4.779440306 | 20789.57
569 | 3.1629659 | 1048.402 | 10.21383404 | 317530.7 | 4.758254737 | 20750.77
570 | 3.096189382 | 1333.867 | 10.62045194 | 313629 | 4.721167522 | 20505.87
571 | 3.035318136 | 1647.76 | 11.03703382 | 311194.5 | 4.712807011 | 20321.95
572 | 2.998917265 | 1940.997 | 11.03795114 | 312382.3 | 4.716966423 | 20349.57
573 | 2.961788688 | 2235.976 | 11.03744651 | 313581 | 4.720946851 | 20377.88
574 | 2.903825567 | 2540.175 | 10.9703473 | 313950.2 | 4.706024639 | 20237.05
575 | 2.827458473 | 2902.287 | 10.97330146 | 313338.1 | 4.694533575 | 20139.54
576 | 2.751265333 | 3262.321 | 10.97202228 | 312758.4 | 4.682972596 | 20042.18
577 | 2.699030566 | 3458.834 | 10.69895351 | 314270.4 | 4.696213845 | 19740.28
578 | 2.654975216 | 3656.351 | 10.45350586 | 316804 | 4.732229697 | 19498.64
579 | 2.588908155 | 4035.465 | 10.55611068 | 316991.7 | 4.735135282 | 19557.98
580 | 2.524116245 | 4405.976 | 10.64427897 | 317286.8 | 4.737943207 | 19617.68
581 | 2.523417318 | 4489.076 | 10.8142894 | 319090.5 | 4.813729759 | 19521.95
582 | 2.510635358 | 4557.967 | 10.94518851 | 319760.2 | 4.863924546 | 19375.94
583 | 2.491467533 | 4646.637 | 11.07467099 | 318801.1 | 4.879451144 | 19260.31
584 | 2.494297745 | 4711.079 | 11.62366275 | 314758.4 | 4.914354619 | 19148.61
585 | 2.457893411 | 4702.903 | 12.14655363 | 306759.2 | 4.828603205 | 18886.81
586 | 2.388139163 | 4925.634 | 12.75338903 | 297798.5 | 4.725314865 | 18797.47
587 | 2.315690877 | 5152.333 | 13.32937049 | 289078.9 | 4.62053177 | 18706.45
588 | 2.215527447 | 5169.152 | 13.97934575 | 275048.9 | 4.348105729 | 18392.23
589 | 2.136563051 | 5213.018 | 14.63991381 | 264464.7 | 4.159296006 | 18160.07
590 | 2.065297166 | 5586.33 | 15.03917936 | 262184.4 | 4.14445095 | 18197.05
591 | 1.989275329 | 5973.171 | 15.42906007 | 259984.9 | 4.129106442 | 18234.88
592 | 1.914291912 | 6243.589 | 15.38410087 | 262449.7 | 4.13448641 | 18210.83
593 | 1.837605901 | 6560.898 | 15.22196282 | 264449.6 | 4.147946313 | 18175.18
594 | 1.762499774 | 6867.637 | 15.05652471 | 266477.4 | 4.161380555 | 18139.67
595 | 1.668940878 | 7185.082 | 14.76352198 | 270793.2 | 4.233753803 | 17948.61
596 | 1.583777192 | 7418.357 | 14.34402517 | 275735.8 | 4.329994881 | 17690.48
597 | 1.49441843 | 7776.585 | 13.96120711 | 279415.3 | 4.39927276 | 17571.77
598 | 1.410643575 | 8101.153 | 13.58560227 | 283037 | 4.469127155 | 17453.45
599 | 1.356143943 | 8093.584 | 12.93850379 | 288328.3 | 4.561258281 | 17160.32
600 | 1.316703789 | 8052.255 | 12.35002694 | 293722.9 | 4.649557742 | 16914.68

601 | 1.289503876 | 8094.868 | 12.01913505 | 296967 | 4.688572353 | 16790.75
602 | 1.266354412 | 8119.277 | 11.68593792 | 300227.8 | 4.727645744 | 16666.27
603 | 1.292943945 | 7912.392 | 11.61663436 | 303038.7 | 4.795302199 | 16590.25
604 | 1.289614307 | 7899.373 | 11.58482182 | 303977.6 | 4.817073228 | 16571.03
605 | 1.287658358 | 7880.472 | 11.55159739 | 304927.5 | 4.838833266 | 16552.24
606 | 1.294612754 | 7725.054 | 11.44667144 | 305273.7 | 4.848148819 | 16366.76
607 | 1.304248836 | 7560.417 | 11.34811447 | 305052.6 | 4.842251187 | 16176.14
608 | 1.30915988 | 7484.236 | 11.03959222 | 306566.5 | 4.824658172 | 16127.32
609 | 1.314950035 | 7404.624 | 10.72629194 | 308108.9 | 4.806878671 | 16078.75
610 | 1.340578097 | 7180.74 | 10.84199598 | 305305.9 | 4.794186297 | 15911.69
611 | 1.367278583 | 6960.794 | 10.95632648 | 302660.2 | 4.781280435 | 15755.33
612 | 1.366597012 | 6891.186 | 10.83886727 | 302508.2 | 4.753004485 | 15684.18
613 | 1.366744522 | 6818.209 | 10.72036939 | 302366.4 | 4.724745461 | 15613.33
614 | 1.38538355 | 6593.762 | 10.41384704 | 302391.2 | 4.673207952 | 15537.08
615 | 1.403345015 | 6402.92 | 10.11822933 | 303221.2 | 4.632415126 | 15500.19
616 | 1.425453849 | 6309.909 | 10.16142452 | 303351.2 | 4.645432873 | 15472.62
617 | 1.44777538 | 6216.883 | 10.20066136 | 303512.3 | 4.658447581 | 15445.25
618 | 1.494173388 | 6039.807 | 10.25772953 | 305063.4 | 4.68299133 | 15421.4
619 | 1.488411104 | 6055.545 | 10.1909809 | 306162.6 | 4.674618893 | 15420.48
620 | 1.483004419 | 6069.802 | 10.12306549 | 307271.2 | 4.666139266 | 15419.86
621 | 1.502586354 | 5942.39 | 10.11015795 | 306518.5 | 4.647881044 | 15378.26
622 | 1.511059306 | 5839.471 | 10.07943919 | 305006.7 | 4.61618678 | 15359.44
623 | 1.519668655 | 5763.187 | 10.29289936 | 302225.2 | 4.612564831 | 15262.79
624 | 1.52835181 | 5686.865 | 10.49760928 | 299514.6 | 4.608632678 | 15166.97
625 | 1.504924093 | 5680.195 | 10.61406219 | 295859.1 | 4.545277009 | 15151.98
626 | 1.479733286 | 5701.879 | 10.78598504 | 292586.3 | 4.48214211 | 15131.04
627 | 1.48597457 | 5657.725 | 11.03422487 | 289755.5 | 4.45262453 | 15115.73
628 | 1.492193528 | 5613.972 | 11.26800322 | 287038.7 | 4.422641902 | 15100.71
629 | 1.50617505 | 5482.126 | 11.23535708 | 286383 | 4.39031478 | 14897.23
630 | 1.520440291 | 5403.557 | 11.18500177 | 286705.4 | 4.387253651 | 14795.74
631 | 1.522481639 | 5388.205 | 11.28725864 | 285719.1 | 4.384638068 | 14757
632 | 1.529331417 | 5370.272 | 11.39195232 | 285607.9 | 4.400924477 | 14715.34
633 | 1.548751809 | 5313.472 | 11.27418575 | 287597.8 | 4.431292562 | 14675.36
634 | 1.565128744 | 5277.097 | 11.16826283 | 289302.6 | 4.453691853 | 14657.65
635 | 1.587723598 | 5200.731 | 11.20516584 | 289809.1 | 4.475522454 | 14601.9
636 | 1.608934827 | 5141.915 | 11.22048203 | 290940.3 | 4.508984008 | 14472.94
637 | 1.606905126 | 5197.299 | 11.26959652 | 291592.7 | 4.53048823 | 14491.04
638 | 1.60166562 | 5232.47 | 11.30722308 | 291130 | 4.530124129 | 14548.59
639 | 1.596516567 | 5267.194 | 11.34309416 | 290680.6 | 4.52966165 | 14606.4
640 | 1.602436254 | 5250.965 | 11.48971766 | 289219.3 | 4.536719089 | 14599.51
641 | 1.607708905 | 5222.869 | 11.65711669 | 287379.3 | 4.529743925 | 14544.57
642 | 1.621170483 | 5197.931 | 12.02049384 | 284336.3 | 4.534165566 | 14523.7
643 | 1.635264865 | 5171.449 | 12.3668955 | 281438.2 | 4.538245098 | 14503.89

644 | 1.592069479 | 5257.775 | 12.63753268 | 277178.6 | 4.439513072 | 14426.74
645 | 1.566625884 | 5290.354 | 12.88271687 | 273449.5 | 4.366182855 | 14360.29
646 | 1.542648469 | 5334.175 | 13.44898524 | 267504.8 | 4.30286659 | 14266.81
647 | 1.489479311 | 5409.913 | 14.089479 | 259168.3 | 4.178855064 | 14056.77
648 | 1.449665965 | 5505.425 | 14.32372968 | 255307.2 | 4.120876818 | 13954.83
649 | 1.445449999 | 5556.2 | 14.45466952 | 254649.2 | 4.136426158 | 13998.53
650 | 1.433730956 | 5627.935 | 14.64652385 | 253528.7 | 4.146906563 | 14029.09
651 | 1.426707939 | 5688.135 | 14.78223603 | 253675.9 | 4.17965333 | 14149.2
652 | 1.412262227 | 5722.666 | 14.84186758 | 252985.8 | 4.199367921 | 14162.63
653 | 1.390476292 | 5736.903 | 14.86266958 | 250658.6 | 4.18906199 | 14059.73
654 | 1.353924308 | 5808.465 | 14.78742672 | 248598.8 | 4.196653761 | 13940.27
655 | 1.313173817 | 5730.737 | 14.50964875 | 244914.9 | 4.177227995 | 13640.29
656 | 1.298826408 | 5607.906 | 14.13093748 | 246234.3 | 4.194184199 | 13432.17
657 | 1.297471772 | 5604.481 | 13.9654812 | 249661.8 | 4.242622393 | 13403.94
658 | 1.298486753 | 5605.873 | 13.87872639 | 252666.9 | 4.287283804 | 13430.03
659 | 1.360672729 | 5415.919 | 13.80506205 | 259619.1 | 4.407438019 | 13447.31
660 | 1.374048824 | 5374.198 | 13.65403308 | 263096.9 | 4.463417804 | 13428.41
661 | 1.388717989 | 5328.829 | 13.50408098 | 266571.3 | 4.519141095 | 13410.61
662 | 1.445606318 | 5082.621 | 13.37742942 | 271062.1 | 4.613621165 | 13338.07
663 | 1.494400618 | 4834.538 | 13.234578 | 274248.9 | 4.678010422 | 13360.24
664 | 1.517713088 | 4746.144 | 13.27711778 | 274871.2 | 4.709652933 | 13433.85
665 | 1.541880118 | 4656.743 | 13.31718871 | 275513.7 | 4.741517817 | 13507.97
666 | 1.608183325 | 4359.15 | 13.45673762 | 275352.6 | 4.779051646 | 13487.83
667 | 1.678422186 | 4025.024 | 13.55522736 | 274747.5 | 4.804390696 | 13334.03
668 | 1.722198125 | 3880.494 | 13.81856887 | 273559.8 | 4.835279694 | 13256.65
669 | 1.76678076 | 3736.607 | 14.07302427 | 272466.3 | 4.866177622 | 13180.17
670 | 1.826667155 | 3472.01 | 14.09283675 | 271702.2 | 4.877326222 | 12998.93
671 | 1.878550443 | 3246.471 | 14.10018233 | 270953.8 | 4.892277428 | 12731.9
672 | 1.904833731 | 3140.14 | 14.2624179 | 269577.6 | 4.91531373 | 12515.33
673 | 1.931458212 | 3033.438 | 14.41266427 | 268290.3 | 4.9384233 | 12298.72
674 | 1.990219277 | 2815.848 | 14.45699258 | 267589.4 | 4.955242702 | 11969.62
675 | 2.045130442 | 2634.584 | 14.49332158 | 267127.1 | 4.96987079 | 11671.26
676 | 2.078188509 | 2549.906 | 14.59286723 | 266562.2 | 4.977259013 | 11577.52
677 | 2.111640684 | 2465.296 | 14.6910255 | 266015.2 | 4.984492485 | 11484.37
678 | 2.148190268 | 2333.931 | 14.76966355 | 265064.9 | 4.989666204 | 11190.84
679 | 2.16067582 | 2280.796 | 14.82703589 | 263631.2 | 4.982362697 | 10871
680 | 2.177197548 | 2297.545 | 14.97104847 | 262886 | 5.017114711 | 10748.9
681 | 2.194118965 | 2314.215 | 15.10987239 | 262196.9 | 5.052173994 | 10628.13
682 | 2.173201634 | 2374.066 | 15.33052474 | 257869.4 | 4.997012432 | 10302.18
683 | 2.146313461 | 2397.53 | 15.53858229 | 252128.3 | 4.923226119 | 10043.3
684 | 2.126011971 | 2376.575 | 15.67240978 | 246427.8 | 4.835681718 | 9768.549
685 | 1.972557396 | 2522.859 | 15.55068429 | 231913.2 | 4.523418268 | 9182.67
686 | 1.868728258 | 2680.244 | 15.82687868 | 219341.2 | 4.333282784 | 8709.758

687 | 1.851147153 | 2755.592 | 16.340023 | 215925.2 | 4.308172067 | 8579.288
688 | 1.838404393 | 2817.8 | 16.86898141 | 212497.8 | 4.281062228 | 8452.571
689 | 1.734450492 | 3308.293 | 17.77481645 | 211354.9 | 4.260987279 | 8573.795
690 | 1.59734852 | 3887.018 | 19.2391564 | 207233 | 4.174635819 | 8867.405
691 | 1.557191014 | 4051.937 | 19.9049578 | 203949.5 | 4.092695899 | 9016.607
692 | 1.535558324 | 4168.178 | 20.57676564 | 200613.1 | 4.011118491 | 9165.017
693 | 1.475808541 | 4463.301 | 21.54685173 | 197025.9 | 3.942628081 | 9297.362
694 | 1.513157426 | 4531.729 | 21.75351518 | 199508 | 4.013792061 | 9285.314
695 | 1.593823095 | 4419.428 | 21.84349929 | 201442 | 4.077574784 | 9292.044
696 | 1.689078507 | 4271.184 | 21.92814502 | 203413.5 | 4.141810194 | 9299.784
697 | 1.736050004 | 4197.167 | 22.02839344 | 203503.7 | 4.15265757 | 9232.175
698 | 1.770755703 | 4066.048 | 22.43538198 | 199800.6 | 4.065278786 | 9220.154
699 | 1.819273243 | 3912.684 | 22.55415929 | 198574.9 | 4.035284358 | 9191.242
700 | 1.872158214 | 3748.719 | 22.66986997 | 197371.8 | 4.004823896 | 9163.227
701 | 1.876108787 | 3722.874 | 22.48731709 | 198648.8 | 4.017634415 | 9146.456
702 | 1.902969367 | 3664.006 | 22.14623322 | 202700.2 | 4.100735436 | 9114.224
703 | 1.946290998 | 3566.128 | 22.16956042 | 204823.4 | 4.188829425 | 8973.084
704 | 1.916103409 | 3664.716 | 21.98289678 | 207519.4 | 4.229961065 | 8979.631
705 | 1.88285323 | 3716.37 | 21.61216692 | 212016.8 | 4.305353086 | 8955.476
706 | 1.820475774 | 3800.77 | 21.17794258 | 216057 | 4.387960634 | 8879.348
707 | 1.757163958 | 3925.872 | 20.95051057 | 218162.3 | 4.436027724 | 8837.759
708 | 1.698283096 | 4038.342 | 20.8887779 | 219664.8 | 4.485038185 | 8772.166
709 | 1.619409557 | 4094.266 | 20.68562918 | 221888.6 | 4.545832345 | 8669.111
710 | 1.529478353 | 4161.527 | 20.76682175 | 222375 | 4.594640847 | 8602.783
711 | 1.445465746 | 4287.674 | 21.08689521 | 220944.8 | 4.601542055 | 8584.401
712 | 1.379100066 | 4375.44 | 21.86506363 | 218250.9 | 4.627693957 | 8524.461
713 | 1.213921418 | 4451.006 | 23.48669242 | 206055.2 | 4.402617891 | 8576.043
714 | 0.99370524 | 4477.67 | 26.32885598 | 180545.6 | 3.858961206 | 8761.554
715 | 0.844321331 | 4528.459 | 28.70762799 | 161687.4 | 3.483911365 | 8882.455
716 | 0.635844144 | 4718.75 | 31.86756083 | 141439.7 | 3.021814006 | 9225.566
717 | 0.403511661 | 4633.333 | 35.16026409 | 110127.5 | 2.316486468 | 9367.329
718 | 0.260780319 | 4581.134 | 36.92794869 | 97224.7 | 2.00250476 | 9451.62
719 | 0.186702823 | 4666.925 | 37.55604387 | 98353.55 | 2.013395011 | 9510.775
720 | 0.111536353 | 4749.85 | 38.1671637 | 99651.14 | 2.022125831 | 9574.218
721 | 0.036297153 | 4806.211 | 38.048094 | 105519 | 2.111411046 | 9628.163
722 | -0.060021186 | 4834.179 | 38.81510754 | 103182.3 | 2.03154665 | 9724.769
723 | -0.148686079 | 4901.52 | 39.33326941 | 99499.99 | 1.960386129 | 9727.681
724 | -0.2328904 | 4959.065 | 39.8467502 | 95841.07 | 1.888609468 | 9732.247
725 | -0.393739957 | 5066.55 | 40.72008126 | 90703.67 | 1.764020123 | 9792.422
726 | -0.454556551 | 5005.858 | 40.97508749 | 89251.23 | 1.72781465 | 9770.894
727 | -0.498845148 | 5008.828 | 41.01701593 | 89840.14 | 1.74739081 | 9739.386
728 | -0.544590285 | 5019.117 | 40.67991662 | 90786.25 | 1.745436581 | 9732.991
729 | -0.564101556 | 4947.947 | 39.81259883 | 97393.47 | 1.86310015 | 9685.699

730 | -0.545546926 | 4849.358 | 38.08626553 | 111386.1 | 2.167135776 | 9537.758
731 | -0.53752465 | 4824.499 | 36.72807486 | 121664.5 | 2.396446935 | 9418.626
732 | -0.538259162 | 4830.018 | 34.71991999 | 132952.1 | 2.599767904 | 9265.135
733 | -0.480715962 | 4712.898 | 32.54014872 | 150836.1 | 3.011195083 | 9024.632
734 | -0.437481682 | 4604.594 | 30.77435445 | 164251.9 | 3.324116611 | 8805.301
735 | -0.424676838 | 4558.9 | 29.89662832 | 169992.1 | 3.435442542 | 8727.575
736 | -0.410545798 | 4510.987 | 28.99171873 | 175851.9 | 3.546800198 | 8651.092
737 | -0.375706038 | 4420.235 | 27.73761282 | 183865.2 | 3.740565134 | 8421.568
738 | -0.338861826 | 4334.516 | 26.43687561 | 191496.8 | 3.94198056 | 8148.794
739 | -0.308933852 | 4270.197 | 25.5354856 | 197460.1 | 4.06996412 | 8066.425
740 | -0.281993754 | 4217.883 | 25.0014854 | 201359.5 | 4.170864855 | 7969.589
741 | -0.237598807 | 4141.372 | 24.1426224 | 208075.7 | 4.360615596 | 7791.812
742 | -0.198135436 | 4078.543 | 23.48983454 | 213907.5 | 4.545515372 | 7599.933
743 | -0.178528173 | 4044.626 | 23.20344969 | 216419.1 | 4.622677121 | 7501.287
744 | -0.160225111 | 4010.536 | 23.12742653 | 218623.6 | 4.699205402 | 7477.278
745 | -0.133058386 | 3957.012 | 22.97311613 | 221670.5 | 4.806614093 | 7399.626
746 | -0.103148943 | 3892.526 | 22.62579484 | 223325.9 | 4.848730305 | 7204.339
747 | -0.087275311 | 3842.994 | 22.50507433 | 224306.4 | 4.899263022 | 7084.083
748 | -0.07847183 | 3812.951 | 22.47755075 | 224656 | 4.925973221 | 7020.67
749 | -0.069211308 | 3782.077 | 22.63526147 | 224254.5 | 4.919277117 | 7025.237
750 | -0.057485295 | 3737.61 | 22.77459476 | 223744.9 | 4.90906386 | 7000.293
751 | -0.03405792 | 3675.572 | 23.09852743 | 223090.6 | 4.955565697 | 6826.587
752 | -0.027142588 | 3653.749 | 23.31033366 | 223333.5 | 4.999056355 | 6790.021
753 | -0.020039762 | 3631.804 | 23.51966302 | 223612 | 5.042324796 | 6755.196
754 | -0.009996406 | 3597.185 | 24.05604376 | 222889.9 | 5.097690786 | 6656.695
755 | -0.005230737 | 3537.746 | 24.40363298 | 219708.5 | 5.080828008 | 6521.941
756 | 0.040339664 | 3356.877 | 26.7000221 | 208628.5 | 4.912852148 | 6453.518
757 | 0.059808695 | 3222.246 | 27.44857598 | 200319.4 | 4.715236375 | 6431.642
758 | 0.069503807 | 2812.087 | 26.23241366 | 172613 | 3.978825447 | 5931.262
759 | 0.060212935 | 2339.067 | 24.44204458 | 137474 | 3.064516244 | 5179.169
760 | 0.064282831 | 2144.041 | 24.82105991 | 122469.2 | 2.68318876 | 4941.178
761 | 0.072384446 | 1944 | 25.49833444 | 108009.1 | 2.25711579 | 4824.596
762 | 0.066723428 | 1793.191 | 25.61963792 | 96539.97 | 1.898978414 | 4666.673
763 | 0.083872201 | 1809.698 | 27.1612321 | 98736 | 1.924284694 | 4823.081
764 | 0.108365407 | 1974.938 | 28.20775686 | 113906.8 | 2.297418069 | 5133.205
765 | 0.123423808 | 2097.189 | 28.26999988 | 125291.6 | 2.565020398 | 5337.086
766 | 0.118454403 | 2252.345 | 26.27665025 | 140919.9 | 2.887388137 | 5451.014
767 | 0.148209167 | 2498.272 | 26.83484953 | 163287.3 | 3.484880489 | 5776.253
768 | 0.171432549 | 2696.507 | 26.89217169 | 181496.6 | 3.973076985 | 5997.094
769 | 0.171970712 | 2777.773 | 26.3108215 | 189084 | 4.147462177 | 6036.053
770 | 0.172030571 | 2859.842 | 25.75342549 | 196646.8 | 4.31937457 | 6076.131
771 | 0.187161105 | 2939.414 | 25.34765052 | 205906.8 | 4.568541602 | 6152.671
772 | 0.198685334 | 2974.738 | 25.24427401 | 210085.8 | 4.674311871 | 6146.696

773 | 0.19899267 | 2987.178 | 25.05969021 | 211231.3 | 4.689817719 | 6116.29
774 | 0.222509321 | 2964.615 | 25.13163122 | 213254.2 | 4.799036495 | 6036.985
775 | 0.236111437 | 2960.991 | 25.35261016 | 214224 | 4.85167066 | 6021.324
776 | 0.246745507 | 2953.774 | 25.52534219 | 214500.9 | 4.870647443 | 6012.887
777 | 0.265687723 | 2923.316 | 25.54494095 | 214338.2 | 4.895660463 | 5900.98
778 | 0.278991426 | 2900.572 | 25.59567523 | 214141.2 | 4.912423348 | 5825.258
779 | 0.297447684 | 2874.197 | 25.9156051 | 214112.8 | 4.834812065 | 5993.341
780 | 0.310423064 | 2855.052 | 25.88924137 | 214117.8 | 4.859829761 | 5899.564
781 | 0.327626431 | 2825.985 | 25.8715157 | 213825.6 | 4.87596874 | 5803.637
782 | 0.333938257 | 2810.149 | 26.40381971 | 212314.1 | 4.854847841 | 5735.146
783 | 0.339897455 | 2803.203 | 26.77924634 | 211467.5 | 4.820483331 | 5815.328
784 | 0.341777128 | 2797.896 | 27.30956786 | 209328.9 | 4.714949969 | 5934.176
785 | 0.330271738 | 2795.94 | 28.41700968 | 204376.7 | 4.571099495 | 5958.705
786 | 0.310803654 | 2802.75 | 29.56148386 | 198762.6 | 4.366208075 | 6097.077
787 | 0.302474868 | 2802.041 | 30.51138376 | 195042.1 | 4.256196934 | 6179.178
788 | 0.289760272 | 2807.854 | 31.13132332 | 192030.8 | 4.149382488 | 6253.272
789 | 0.271075502 | 2807.527 | 31.89380309 | 186876.1 | 3.97159722 | 6328.562
790 | 0.289798763 | 2755.038 | 32.664405 | 182951.2 | 3.880841878 | 6280.933
791 | 0.301615619 | 2733.648 | 32.87180694 | 182148.6 | 3.886080235 | 6244.198
792 | 0.313588597 | 2712.191 | 33.07705842 | 181363.2 | 3.890865398 | 6208.275
793 | 0.352629451 | 2652.506 | 33.28042781 | 181313.5 | 3.906717868 | 6150.687
794 | 0.371734727 | 2622.225 | 33.43963549 | 180210.9 | 3.862894457 | 6123.789
795 | 0.380785277 | 2613.641 | 33.92180847 | 178634.3 | 3.792591204 | 6149.13
796 | 0.399621967 | 2595.954 | 34.50301902 | 178911.9 | 3.791223446 | 6209.354
797 | 0.408569328 | 2582.496 | 34.95030055 | 177690.6 | 3.742129035 | 6223.925
798 | 0.415823783 | 2572.128 | 35.40369267 | 176042.9 | 3.666513184 | 6238.841
799 | 0.420456989 | 2567.942 | 36.18392706 | 174663.7 | 3.581305956 | 6346.996
800 | 0.4207835 | 2555.634 | 36.41001712 | 172661.8 | 3.495954898 | 6355.829
801 | 0.426546801 | 2542.733 | 36.49262686 | 172010.8 | 3.466035336 | 6354.447
802 | 0.431773034 | 2526.354 | 36.36787973 | 171912.1 | 3.452297783 | 6289.088
803 | 0.457091261 | 2492.646 | 36.43131247 | 172194 | 3.482736032 | 6223.173
804 | 0.49012981 | 2456.42 | 36.24889811 | 173928.5 | 3.55049149 | 6149.441
805 | 0.519803644 | 2418.163 | 36.5729787 | 174981.4 | 3.574781252 | 6138.303
806 | 0.531047645 | 2404.407 | 36.65900076 | 175185.3 | 3.605576263 | 6083.367
807 | 0.537401423 | 2385.659 | 36.7894249 | 174306.4 | 3.596524723 | 6028.838
808 | 0.530287748 | 2380.792 | 38.38165347 | 170301.7 | 3.431361245 | 6247.002
809 | 0.468919083 | 2410.729 | 40.71117981 | 160209.7 | 3.128530324 | 6423.86
810 | 0.41621095 | 2442.424 | 42.97987634 | 151252.2 | 2.886379279 | 6575.505
811 | 0.380935736 | 2460.271 | 46.0919549 | 143759.9 | 2.593299757 | 6900.705
812 | 0.263040273 | 2507.755 | 50.60820123 | 123791.6 | 2.057452352 | 7209.766
813 | 0.13659891 | 2538.952 | 55.59410623 | 100715.7 | 1.490790761 | 7467.268
814 | 0.022677158 | 2552.147 | 62.16809446 | 75121.54 | 0.964826255 | 7666.432
815 | -0.018374105 | 2550.143 | 63.83610382 | 70022.88 | 0.693382813 | 7865.168

816 | -0.05646504 | 2542.971 | 65.08840607 | 63840.72 | 0.524733658 | 7895.222
817 | -0.081084096 | 2505.592 | 65.59157619 | 59868.67 | 0.421519322 | 7830.894
818 | -0.046265738 | 2436.637 | 64.47388524 | 64868.35 | 0.459577905 | 7785.851
819 | -0.004310919 | 2369.328 | 62.0825818 | 73400.97 | 0.560831925 | 7706.489
820 | 0.012724172 | 2335.42 | 60.5952039 | 78432.89 | 0.568173896 | 7716.396
821 | 0.020568804 | 2314.824 | 57.5065099 | 84690.49 | 0.686597349 | 7537.865
822 | 0.032918433 | 2264.903 | 55.97269886 | 88657.32 | 0.793804008 | 7365.627
823 | 0.059257745 | 2213.778 | 54.16460326 | 95744.51 | 0.936321338 | 7248.717
824 | 0.091826154 | 2165.517 | 51.58271302 | 106929.6 | 1.038128263 | 7260.78
825 | 0.099740076 | 2144.256 | 49.92097275 | 112471.8 | 1.116948451 | 7185.329
826 | 0.109855716 | 2120.888 | 48.71113076 | 117187.1 | 1.138801972 | 7210.005
827 | 0.118477609 | 2066.166 | 47.51803157 | 121219.2 | 1.161436115 | 7196.406
828 | 0.12751722 | 2001.503 | 44.26275501 | 129050.4 | 1.232128842 | 7074.522
829 | 0.136324469 | 1938.274 | 42.6721622 | 133018.3 | 1.272366927 | 7003.581
830 | 0.142222974 | 1908.536 | 41.21790602 | 136870.8 | 1.313983602 | 6949.521
831 | 0.151619653 | 1876.754 | 38.70354257 | 144176.8 | 1.371497611 | 6899.998
832 | 0.172292435 | 1818.734 | 35.37168304 | 153332.5 | 1.547891742 | 6694.042
833 | 0.203907985 | 1765.869 | 32.72638491 | 162828 | 1.739230278 | 6543.466
834 | 0.244785551 | 1713.435 | 29.96516342 | 173449.1 | 1.957855661 | 6392.486
835 | 0.259115804 | 1700.621 | 26.50288463 | 183678.2 | 2.069039316 | 6323.69
836 | 0.282423885 | 1668.162 | 24.11588665 | 190892.4 | 2.172202334 | 6215.054
837 | 0.324775225 | 1625.935 | 22.43899524 | 198864.9 | 2.427942012 | 6021.498
838 | 0.359872376 | 1592.416 | 20.65887577 | 206309.4 | 2.685367335 | 5797.178
839 | 0.400838488 | 1543.462 | 17.58308274 | 216351 | 2.896280291 | 5598.427
840 | 0.412737486 | 1526.76 | 16.58675084 | 219445 | 2.969346413 | 5509.736
841 | 0.424523375 | 1510.082 | 15.63223661 | 222450.9 | 3.041777336 | 5421.074
842 | 0.469415468 | 1453.634 | 12.75527376 | 230749.7 | 3.267218426 | 5190.525
843 | 0.504563119 | 1395.499 | 10.80254295 | 236232.3 | 3.326751601 | 5098.281
844 | 0.529251487 | 1361.793 | 10.42037978 | 238144.7 | 3.426613606 | 5010.822
845 | 0.543224537 | 1342.793 | 9.627421028 | 240219.5 | 3.439444717 | 5016.55
846 | 0.556640757 | 1329.504 | 7.344122303 | 245868.6 | 3.528246054 | 4942.477
847 | 0.567975597 | 1292.651 | 5.112923214 | 249840.5 | 3.549609648 | 4828.175
848 | 0.588913213 | 1249.105 | 3.464942713 | 251559.7 | 3.530616382 | 4835.098
849 | 0.586619701 | 1225.318 | 2.403036961 | 251639.7 | 3.547000074 | 4693.695
850 | 0.587960582 | 1187.888 | 1.073581616 | 251580.8 | 3.524842005 | 4578.151
851 | 0.592286543 | 1156.399 | -0.849353776 | 253856.5 | 3.411448256 | 4627.137
852 | 0.603447678 | 1133.639 | -2.474413937 | 255391.7 | 3.380857555 | 4662.204
853 | 0.596906481 | 1106.471 | -2.146702245 | 251380.7 | 3.349346506 | 4546.92
854 | 0.600458993 | 1084.046 | -1.695733052 | 249702.5 | 3.383596603 | 4430.297
855 | 0.618855857 | 1067.697 | -3.074423148 | 254975.8 | 3.466168251 | 4399.429
856 | 0.626305567 | 1067.131 | -3.81749288 | 258127.6 | 3.51880871 | 4383.597
857 | 0.633883643 | 1061.335 | -3.902802134 | 259945 | 3.536287399 | 4391.12
858 | 0.655635833 | 1037.15 | -3.969317947 | 262794.1 | 3.594169596 | 4371.342

859 | 0.66531555 | 1040.44 | -4.342072169 | 265177.5 | 3.642694514 | 4412.814
860 | 0.671241957 | 1035.148 | -4.172710748 | 265854.6 | 3.691587111 | 4371.378
861 | 0.676043071 | 1019.093 | -5.829783005 | 269280.3 | 3.707469599 | 4306.885
862 | 0.678587352 | 1008.161 | -6.480165229 | 269506 | 3.673728056 | 4339.799
863 | 0.681052142 | 997.3743 | -7.125404291 | 269702.8 | 3.639754407 | 4372.603
864 | 0.695850575 | 939.7268 | -8.026063476 | 267907.5 | 3.592758369 | 4263.24
865 | 0.695511607 | 913.2515 | -9.792132225 | 267735.5 | 3.516780897 | 4249.948
866 | 0.69337276 | 903.8066 | -9.793257958 | 266066.4 | 3.537213725 | 4188.686
867 | 0.697558932 | 888.8774 | -10.31588539 | 267520 | 3.546129735 | 4143.582
868 | 0.701748781 | 873.8669 | -10.83503907 | 268971 | 3.553670968 | 4100.31
869 | 0.699243735 | 888.5477 | -12.31013015 | 273357.5 | 3.541444174 | 4203.705
870 | 0.712594142 | 873.0847 | -14.71575363 | 279375.7 | 3.451457299 | 4381.766
871 | 0.718073704 | 857.4306 | -14.48617011 | 279549.7 | 3.590003388 | 4171.415
872 | 0.728794813 | 842.0541 | -14.74903533 | 279899.7 | 3.535271087 | 4263.065
873 | 0.733339411 | 834.9826 | -14.88398637 | 279761 | 3.49007952 | 4343.357
874 | 0.737143664 | 818.2899 | -15.9494114 | 281605.9 | 3.455462362 | 4349.28
875 | 0.737412954 | 809.4464 | -17.80930207 | 284624.5 | 3.416677621 | 4374.705
876 | 0.739301965 | 799.2059 | -19.12103652 | 286469.5 | 3.393120564 | 4389.805
877 | 0.725313318 | 797.1601 | -19.57454254 | 286791.9 | 3.442097162 | 4235.108
878 | 0.73059549 | 764.0284 | -20.2215329 | 287149.6 | 3.465135183 | 4107.279
879 | 0.733646633 | 766.2975 | -20.48495491 | 286585.2 | 3.409954243 | 4239.594
880 | 0.734283219 | 756.2713 | -20.99524379 | 286887 | 3.390746412 | 4238.763

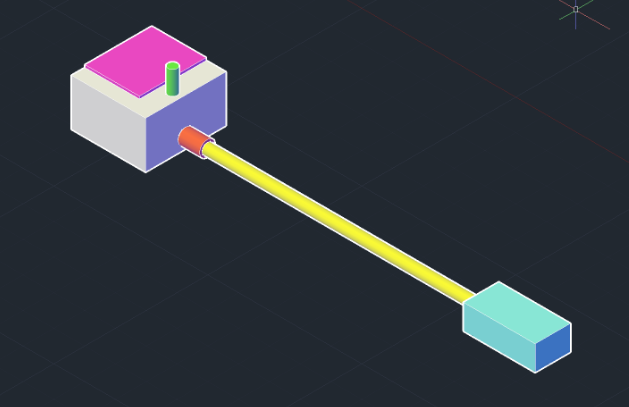
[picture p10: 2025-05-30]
Schematics/Mechanical Drawing.png

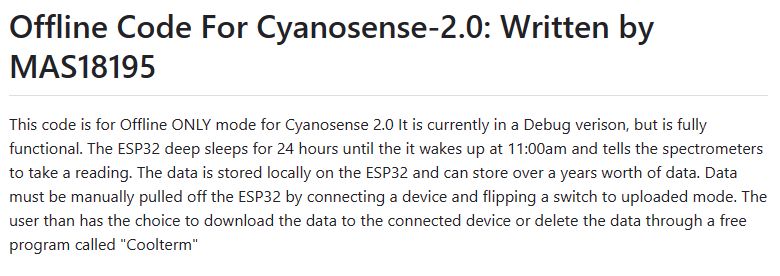
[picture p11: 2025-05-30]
Code/Offline and Test Code/ESP32_Dual_Spectrometer_SPIFFS_Sleep_Serial_01/README.png

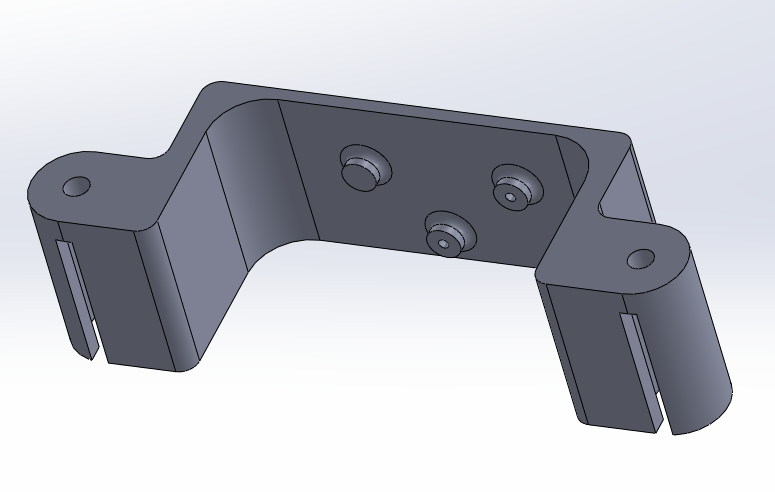
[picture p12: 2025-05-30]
3D Printed Parts/Spectrometer Mount/Spectrometer Mount.PNG

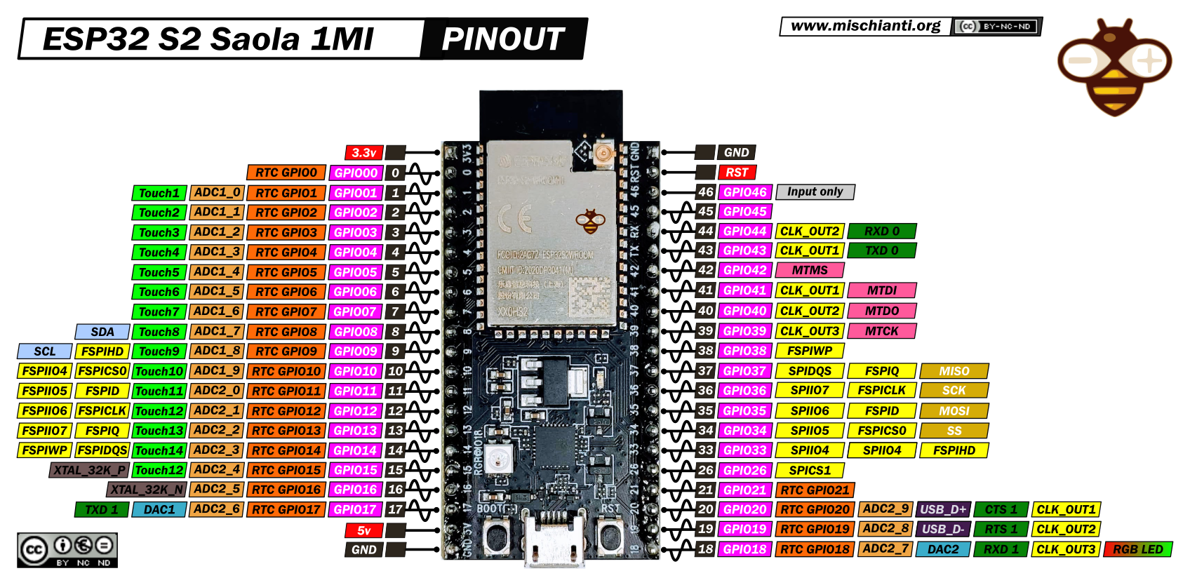
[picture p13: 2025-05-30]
Schematics/ESP32-S2-Saola-1MI-pinout-mischianti.png

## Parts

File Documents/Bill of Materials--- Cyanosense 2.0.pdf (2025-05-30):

## Cyanosense 2.0 Bill of Materials

This is the Finalized Bill of Materials for Cyanosense 2.0. Note that the Prices are based

on the EXACT number to build the Prototype, unless noted otherwise. Tax and any

shipping costs are NOT included. The total cost to build the Prototype was $1,300.33,

which is over two times cheaper than Cyanosense 1.0.

Item | QTY | Price | Link | Reason
| | Electronics Parts
Hamamatsu C12880MA Micro-Spectrometer | 2 ($350 Each) | $700 | BO-HAMA-C12880-V2-SENSOR GroupGets LLC | Development Boards, Kits, Programmers | DigiKey (https://www.digikey.com/en/products/detail/groupgets-llc/BO-HAMA-C12880-V2-SENSOR/14306449) | Spectrometers for Cyanosense 2.0
TLP3556A Photorelay | 1 | $4.20 | TLP3556A(TP1,F Toshiba | Mouser (https://www.mouser.com/ProductDetail/Toshiba/TLP3556ATP1F?qs=r5DSvlrkXmJCPc02EG%252Bwtw%3D%3D) | Turns Sensors On and Off
ROCKBLOCK 9603 Iridium Satellite Modem | 1 | $299.95 | RockBLOCK 9603 with USB Cable - Iridium Satellite Modem Bundle : ID 4521 Adafruit (https://www.adafruit.com/product/4521) | Satellite Communication to Transfer Lab Data
ROCKBLOCK 9603 Accessory Cable | 1 | $4.95 | RockBLOCK 9603 Accessory Cable : ID 4529 : Adafruit (https://www.adafruit.com/product/4529) | Adaptor Cable to ESP Interface
M1600HCT-P-SMA Iridium Passive Anetnna | 1 | $64.95 | Iridium/GPS/GLONASS Passive Antenna -GPS-16838 - SparkFun (https://www.sparkfun.com/products/16838) | Antenna for the Iridium Modem
SMA Male with Waterproof Ring SMA Female Bulkhead Antenna | 1 | $3.63 | RedYutou SMA Male to with Waterproof Ring SMA Female Bulkhead nut o-Ring RG316 (https://www.amazon.com/dp/B082964WZ3?psc=1&ref=ppx_yo2ov_dt_b_product_details) | Antenna Cable for Iridium Modem

Cable 30cm

ESP32-S2 Saola Dev Kit | 1 | $14.50 | ESP32-S2 Saola 1R Dev Kit featuring ESP32-S2 WROVER : ID 4693 Adafruit (https://www.adafruit.com/product/4693) | Microcontroller for the system
DS3231 Real Time Clock | 1 | $3.80 | Wishiot DS3231 Real Time Clock Module High Precision (amazon.com) (https://www.amazon.com/DS3231-Precision-AT24C32-Arduino-Raspberry/dp/B07V68443F) | RTC to control wakeup and sleep for ESP32-S2
DIYHZ 1P2T SPFT Vertical Slide Switch | 1 | $0.09 | Amazon.com: DIYhz 100Pcs High Knob 3 Pin 2 Position 1P2T SPDT Vertical Slide Switch with PCB Panel for Arduino, 0.5 Amp, 50V DC, 2 mm (https://www.amazon.com/dp/B07BD1SPYG?psc=1&ref=ppx_yo2ov_dt_b_product_details) | Slide Switch used to put ESP32-S2 to Download Data Mode or Normal Operation
Voltaic 2 Watt Solar Charger Kit (Includes Voltaic V25 Battery, 2W Solar Panel, and adaptor) | 1 | $59.99 | 2 Watt Solar Panel Kit with USB Battery Pack (voltaicsystems.com) (https://voltaicsystems.com/2-watt-kit/) | Solar Panel and Battery
0.5ft Micro USB Cable to USB | 1 | $4.99 | CableCreation Short USB to Micro USB Cable 0.5 FT, USB2.0 Micro USB (amazon.com) (https://www.amazon.com/dp/B07CKXQ9NB?ref=ppx_yo2ov_dt_b_product_details&th=1) | Connects ESP32-S2 to Battery
SchmalzTech Premium 470 Position Breadboard ST-BB- | 2 ($8.99 Each) | $17.98 | SchmalzTech Premium 470 Position Breadboard (https://www.amazon.com/dp/B0B1XGCFGW?psc=1&ref=ppx_yo2ov_dt_b_product_details) | Breadboard for System

470

Jumper Wire Kit | 1 | $11.99 (Not Exact) | 560 Pieces Jumper Wire Kit 14 Lengths Assorted Preformed Breadboard Jumper Wire Amazon.com (https://www.amazon.com/AUSTOR-Lengths-Assorted-Preformed-Breadboard/dp/B07CJYSL2T) | Wires for Breadboard
120pcs 10cm Breadboard Jumper Wires Assorted Kit | 1 | $6.98 (Not Exact) | Amazon.com: EDGELEC 120pcs 10cm Breadboard Jumper Wires Assorted Kit (https://www.amazon.com/dp/B07GD1XFWV?ref=ppx_yo2ov_dt_b_product_details&th=1) | Jumper Wires for RTC
120pcs 40cm Breadboard Jumper Wires Assorted Kit | 1 | $11.99 (Not Exact) | Amazon.com: EDGELEC 120pcs 40cm Breadboard Jumper Wires Assorted Kit (https://www.amazon.com/dp/B07GD1TH2K?ref=ppx_yo2ov_dt_b_product_details&th=1) | Jumper Wires for Spectrometers

Mechanical Parts

TICONN Waterproof Electrical Junction Box IP67 (5.9”x5.9”x3.5”) | 1 | $19.99 | TICONN Waterproof Electrical Junction Box IP67 ABS Plastic Enclosure with Hinged Cover with Mounting Plate, Wall Brackets, Cable Glands (Off-White, 5.9"x5.9"x3.5") (amazon.com) (https://www.amazon.com/dp/B0B87VR84G?ref=ppx_yo2ov_dt_b_product_details&th=1) | Electronics Housing
3/4in PVC 1-Gang Type FSE Box | 1 | $7.68 | Kraloy 1-Gang Gray PVC Weatherproof New Work/Old Work Standard Rectangular (https://www.lowes.com/pd/Kraloy-PVC-3-4-in-FSE-Single-Gang-Box-91-Hub-93/5001212811) | Sensor Housing

| | | Exterior Electrical Box in the Electrical Boxes department at Lowes.com (https://www.lowes.com/pd/Kraloy-PVC-3-4-in-FSE-Single-Gang-Box-91-Hub-93/5001212811)
TayMac 1-Gang Rectangle Plastic Weatherproof Electrical Box Cover | 1 | $3.58 | TayMac 1-Gang Rectangle Plastic Weatherproof Electrical Box Cover in the Electrical Box Covers department at Lowes.com (https://www.lowes.com/pd/TayMac-1-Gang-Rectangle-Plastic-Weatherproof-Electrical-Box-Cover/5004945479) | Cover for Sensor Housing
CANTEX 3/4in 10ft Schedule 40 PVC Conduit | 1 | $2.06 | CANTEX 3/4-in x 10-ft Non-metallic Schedule 40 PVC Conduit in the Conduit department at Lowes.com (https://www.lowes.com/pd/CANTEX-Common-3-4-in-Actual-75-In-Non-Metallic-Pvc-10-ft-Conduit/3568512) | Used to Connect Sensor and Electronic Housings. Cut to 2ft.
CANTEX 3/4in Schedule 40 PVC Bushing Connector Conduit Fitting | 1 | $0.60 | CANTEX 3/4-in Schedule 40 Schedule 80 PVC Bushing Connector Conduit Fittings in the Conduit Fittings department at Lowes.com (https://www.lowes.com/pd/CANTEX-3-4-in-Bushing-Connector-Schedule-40-PVC-Compatible-Schedule-80-PVC-Compatible-Conduit-Fitting/1000321591) | Attaches PVC Pipe to Electronics Housing
Sigma ProConnex 3/4-in Zinc-plated Steel Conduit Locknut | 1 | $0.39 | Sigma ProConnex 3/4-in Zinc-plated Steel Conduit Locknut Conduit Fittings (2-Pack) in the Conduit Fittings department at Lowes.com (https://www.lowes.com/pd/Sigma-Electric-ProConnex-3-4-in-Conduit-Locknut-Intermediate-Metal-Conduit-Compatible-Galvanized-Rigid-Conduit-Compatible-Rigid-Metal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) | Screws the Bushing Connector to the Electronics Housing

Hillman 1-in Zinc-plated Standard Flat Washer | 1 | $0.78 | Hillman 1-in Zinc-plated Standard Flat Washer in the Flat Washers department at Lowes.com (https://www.lowes.com/pd/Hillman-1-Count-x-2-in-Zinc-Plated-Standard-SAE-Flat-Washer/3006230) | Adds Support to the Inside of the Electronics Housing to prevent flex
1-1/2 Inch Oversize Union Washer Flat Plumbing Slip Joint Washer Rubber Flat Washer | 1 | $0.30 | Amazon.com: 30 Pack 1-1/2 Inch Oversize Union Washer Flat Plumbing Slip Joint Washer Rubber Flat Washer (https://www.amazon.com/dp/B09TPGN29W?psc=1&ref=ppx_yo2ov_dt_b_product_details) | Waterproofs Electronics Box to Pipe Connection
Uxcell M3x30mm Round Aluminium Column Standoffs | 4 | $4.60 | Amazon.com: uxcell 10Pcs M3 x 30mm Round Aluminum Column Alloy Standoff (https://www.amazon.com/dp/B01MYBB70W?ref=ppx_yo2ov_dt_b_product_details&th=1) | Standoff to Support Top Layer in Electronics Box
Uxcell M3x16mm Thumb Screws | 4 | $5.20 | Amazon.com: uxcell M3x16mm Knurled Head Thumb Screws Black 10pcs (https://www.amazon.com/dp/B01MSLME5A?psc=1&ref=ppx_yo2ov_dt_b_product_details) | Thumb Screws to screw down Top Layer
Hillman 4/40 Hex Machine Nuts | 4 | $0.24 | Hillman 140009 Hex Machine Screw Nuts, 4-40, Zinc, 100 Piece: Amazon.com (https://www.amazon.com/Hillman-140009-Machine-Screw-Piece/dp/B001B2QP3C?s=industrial) | Nuts to screw Solar Panel
M3x Screws | 4 | $0.94 | Amazon.com: uxcell M3x10mm Machine Screws Pan Phillips Cross Head Screw 304 Stainless Steel Fasteners Bolts 30Pcs (https://www.amazon.com/uxcell-M3x10mm-Phillips-Stainless-Fasteners/dp/B07MF2ZTBG?cv_ct_cx=m3x10%2Bmachine%2Bscrews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) | Screws Standoffs to Mounting Plate in Electronics House
Microscope Cover Glass Slips | 2 | $8.99 (Not Exact) | MOTUO 50 Pieces Microscope Slides and (https://www.amazon.com/dp/B095N8DNY1?psc=1&ref=ppx_yo2ov_dt_b_product_details) | Cover Glass (20mm x 20m x

| | | 100pcs Pre-Cleaned 20mm x 20mm Microscope Cover Slips Glass Amazon.com (https://www.amazon.com/dp/B095N8DNY1?psc=1&ref=ppx_yo2ov_dt_b_product_details) | 0.13-0.17mm) were used as the lens for the Sensor Housing
GE Advanced Silicone | 1 | $14.99 (Not Exact) | GE Advanced Silicone Window And Door Sealant Clear, 2.8 Oz. (amazon.com) (https://www.amazon.com/GE-GE500-Silicone-Window-Squeeze/dp/B000M2UPAG) | Sealed Solar Panel and Cable for Waterproofing. Was also used to attach glass lends in Sensor Hosuing
Miscellaneous | 1 | $20 (Not Exact) | This Covers TPU Material used for 3D Printed FOV Adaptor, PETG Material Used for the other 3D Printed Parts, and Foam Pads used for Battery
Total Cost: | | $1,300.33

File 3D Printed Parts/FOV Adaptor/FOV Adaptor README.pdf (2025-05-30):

Hamamatsu C12880MA Spectrometer FOV Adaptor

- This adaptor slips on and reduces the FOV of the sensor form 180˚ to 26˚
- One adaptor per sensor.
- The sharp corner (the corner with the triangle) should be lined up with the sharp corner of the sensor when installing. (This is shown in red on Image 1 and 2)
- The adaptor should be printed using TPU

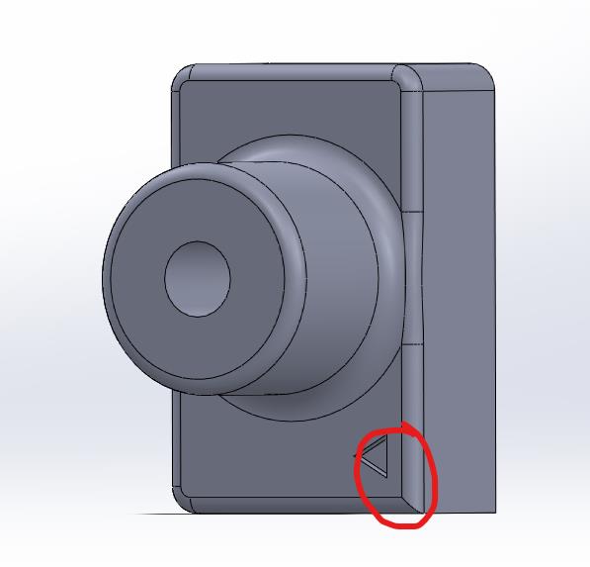
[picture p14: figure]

Image 1

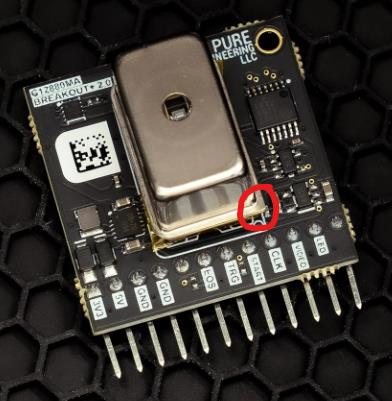
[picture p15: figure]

Image 2

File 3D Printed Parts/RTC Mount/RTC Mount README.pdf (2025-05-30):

### RTC Mount

- Mounts the RTC to the side of the breadboard
- The RTC Mount should be printed using PETG or similar material

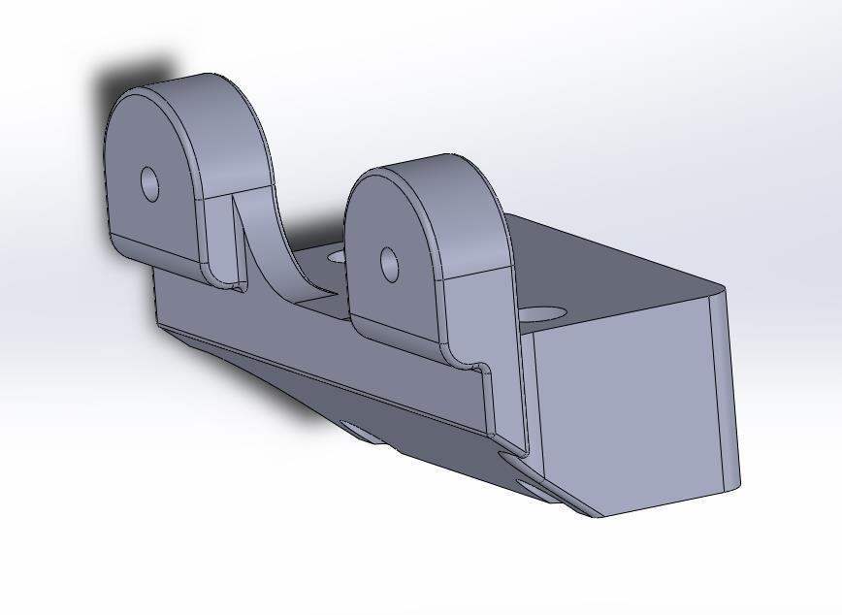
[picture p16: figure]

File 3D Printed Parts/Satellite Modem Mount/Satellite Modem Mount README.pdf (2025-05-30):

## Satellite Modem Mount

- Allows RockBLOCK Iridium 9603 Modem to be mounted.
- Requires the Electronics Housing to be modified by trimming the bottom base plate.
- Image 2 shows the location.
- Image 3 shows the dimensionsof the trimming.
- The Sat Modem Mount should be printed using PETG or similar material

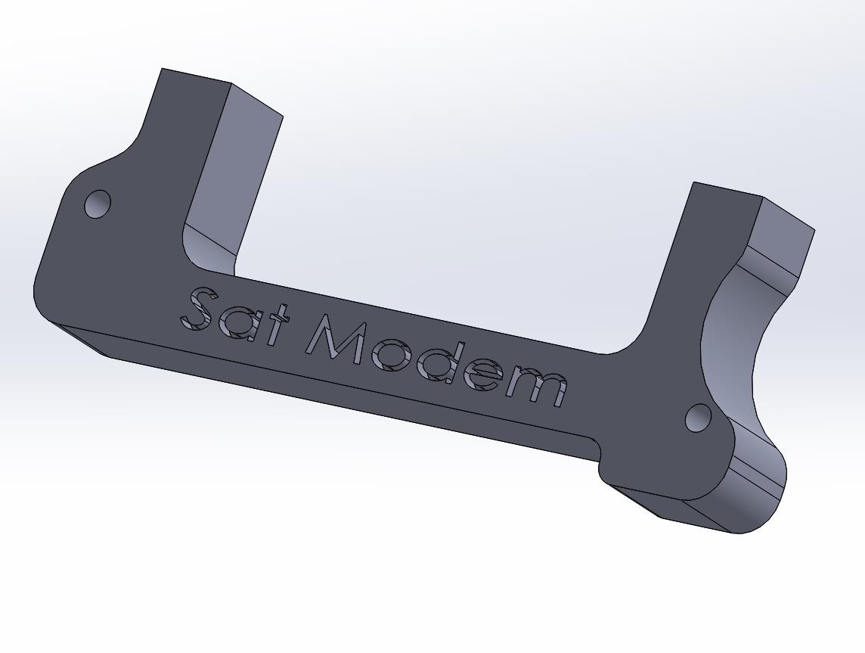
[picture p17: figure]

Image 1

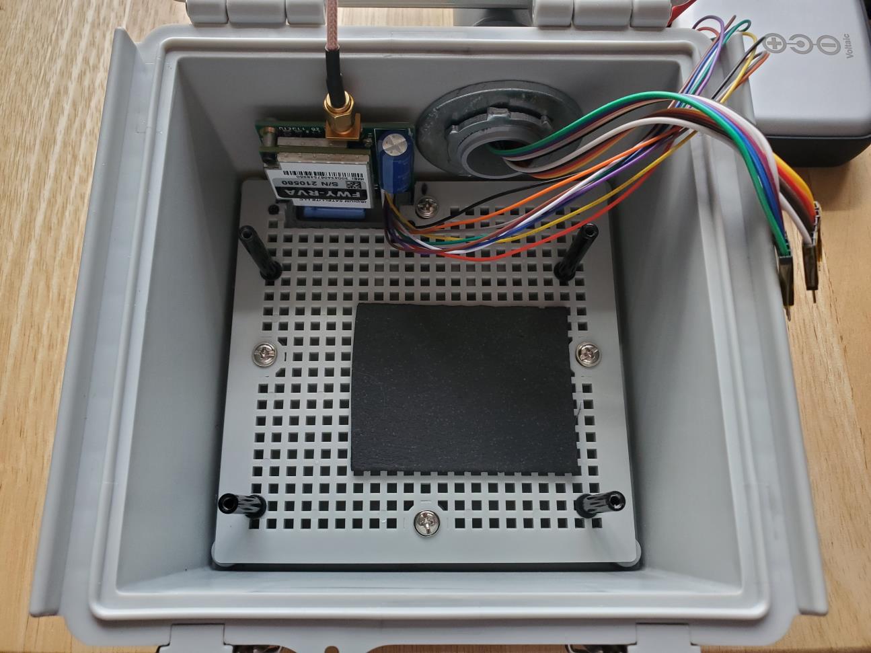
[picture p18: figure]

Image 2

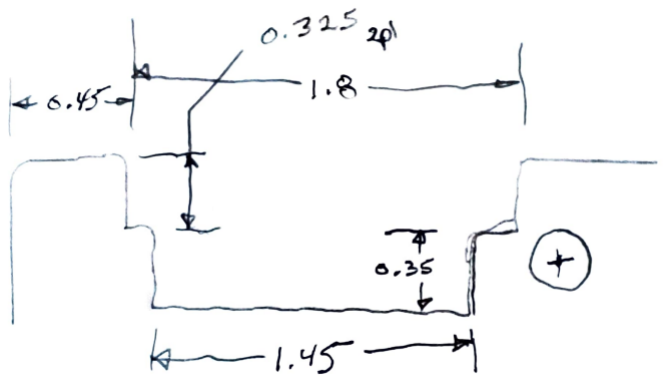
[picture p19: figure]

Image 3

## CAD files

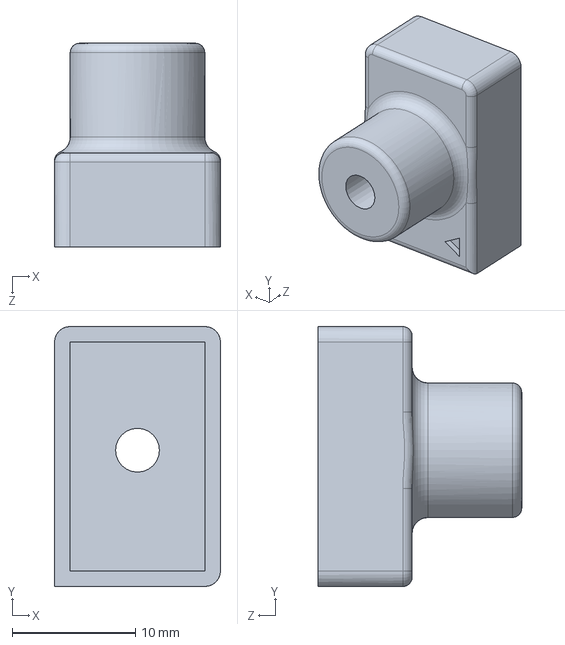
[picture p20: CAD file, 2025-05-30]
3D Printed Parts/FOV Adaptor/FOV Adaptor.SLDPRT
13.5 x 21.1 x 16.5 mm

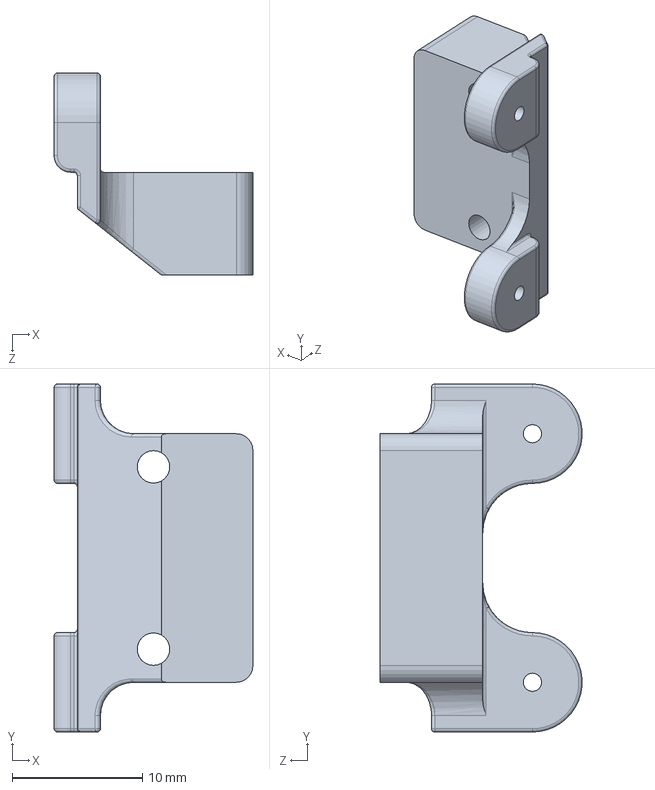
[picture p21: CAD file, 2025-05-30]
3D Printed Parts/RTC Mount/RTC Mount.SLDPRT
15.2 x 26.7 x 15.5 mm

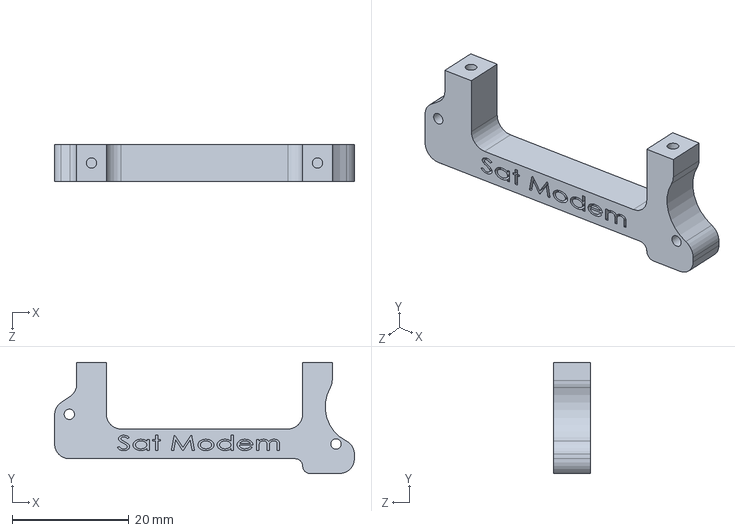
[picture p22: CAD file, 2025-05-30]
3D Printed Parts/Satellite Modem Mount/Sat Modem Mount.SLDPRT
51.4 x 19.0 x 6.35 mm

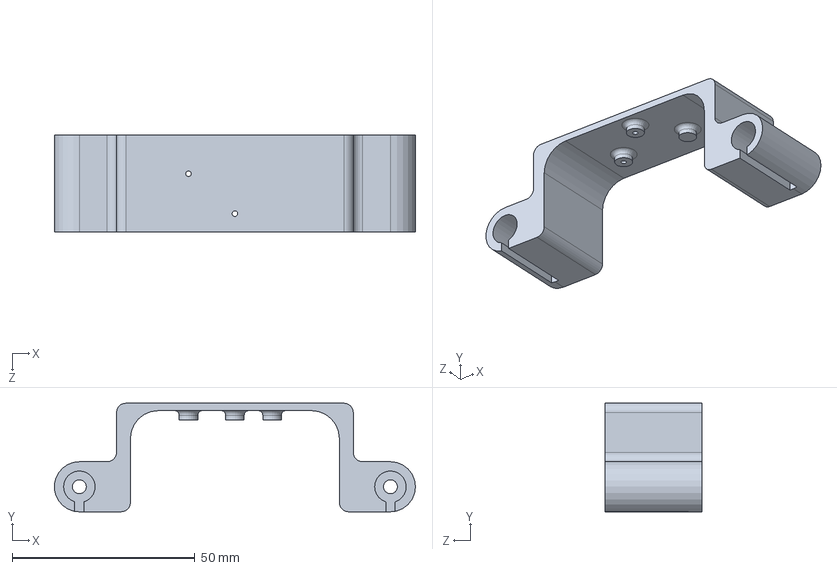
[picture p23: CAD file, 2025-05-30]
3D Printed Parts/Spectrometer Mount/Spectrometer Mount.SLDPRT
98.8 x 29.7 x 26.7 mm

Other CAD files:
3D Printed Parts/FOV Adaptor/FOV Adaptor.STL
3D Printed Parts/RTC Mount/RTC Mount.STL
3D Printed Parts/Satellite Modem Mount/Sat Modem Mount.STL
3D Printed Parts/Spectrometer Mount/Spectrometer Mount.STL

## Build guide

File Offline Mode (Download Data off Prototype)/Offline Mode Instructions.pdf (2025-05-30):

Cyanosense 2.0 Offline Mode Instructions:

1) Disconnect Battery USB from ESP32
2) Flip the Switch to “Download Data Mode” (Flip Switch Towards USB)
3) Connect Device to ESP32 through USB
4) Open CoolTerm or Double Click “Cyanosense 2.0.stc”
5) Select the Correct Serial Port and make sure baud rate is set to 115200
6) Click Connect Device
a. If no prompt shows click RST on ESP32
7) If there is no Terminal Window, enable it in Settings (however if “Cyanosense

2.0.stc” was used, it should already be there)

8) Go to Connection, Capture Text/Binary To File, Start
9) A window should open asking you to save the file. Save it to where you want it,

rename it to what you want, and add “.csv” at the end.

10)Type “G” in Terminal Window and Press Enter

11) Go to Connection, Capture Text/Binary To File, Stop
12) If you want delete to downloaded spectral data off the ESP32, type “D” in

Terminal Window and Press Enter.

13) Disconnect Device from ESP32

14)Flip Switch to “Normal Operation Mode” (Flip Switch Away from USB)

15) Plug Battery USB to ESP32

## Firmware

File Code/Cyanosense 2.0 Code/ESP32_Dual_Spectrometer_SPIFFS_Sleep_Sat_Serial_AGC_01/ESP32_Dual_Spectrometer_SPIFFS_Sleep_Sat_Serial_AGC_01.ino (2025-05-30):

// This reads the Hammamatsu Spectrometers 288 channels and presents the data to the serial port
// where the host sends request for the data when the mode switch is set to upload mode
// The data is then streamed from LittleFS via the serial port in csv format
// In normal mode the scan will complete and the ESP32 will enter deep sleep and be woken by the
// alarm from the RTC module at the programmed time

// This has averaging added to the scan channel

// LittleSPIFFS is used to store and retrieve the sensor calibration coefficients
// which are applied to each of the 288 pixel channels

// Two spectrometers have been incorporated

// There is the ability to adjust the integration time independently for both sensors

// Added deep sleep, RTC clock, and second serial port with word to byte conversion and
// Rockblock 9603 sat modem
// Two sat modem transmissions are required, to transmit 160 intensity values for each sensor

// Manual upload capability to PC with keyboard commands with ~one year of data storage
// Added auto delete mechanism before memory overflow occurs 

// Automatic Gain Control (AGC) was incorporated to compensate for varying degrees of light conditiond

// version ESP32-S2 04/17/2023 build 2.0.7

              
// *************** Saola ESP32-S2 PIN OUTS ***************
//    0-10 GPIO0-10    ADC1 Input, max 3.3V
//    3    GPIO3   IO, wake from deep sleep 
//    9    GPIO9   IO, SCL (clock line)
//    8    GPIO8   IO, SDA (data line)
//    16   GPIO16  IO, 
//    17   GPIO17  IO, DAC1, TXD1
//    18   GPIO18  IO, DAC2, RXD1
//    19   GPIO18  IO, ADC2-8, USBD-, RTS1
//    38   GPIO38  IO, FSPIWP
//    43   GPIO43  IO, TXD0
//    44   GPIO44  IO, RXD0
//    45   GPIO45  IO, 
//----------------------------------------------------------------------------------------


#include <LittleFS.h>
#include <esp_sleep.h>
#include <RTClib.h>
#include <IridiumSBD.h>
#include <driver/adc.h>


// spectrometer 
#define SPEC_ST      7                   // sensor start pin
#define SPEC_CLK     6                   // sensor clock pin
// ADC1_CHANNEL_0                        // GPIO-1 ADC1 channel 0 for API ADC call
// ADC1_CHANNEL_1                        // GPIO-2 ADC1 channel 1 for API ADC call
///#define SPEC_VIDEO_UP   1                // ADC1 channel 0 for Arduino ADC call
///#define SPEC_VIDEO_DWN  2                // ADC1 channel 1 for Arduino ADC call
#define WAKEUP_PIN   3                   // GPIO_NUM_3 used by RTC SQW for deep sleep wakeup
#define RELAY           16               // 5V spectrometer power enable/disable pin
#define UPLOAD_SWITCH 45                 // data upload mode switch pin
#define SPEC_CHANNELS   289              // Spectrum Pixel Channel Bins + 1 because <= does not work
#define DATASTART  30                    // start index of data to send to sat modem (actual, 30) (testing, 30)
#define DATAEND  190                     // end index of data to send to sat modem (actual, 190) (testing, 50)
#define MINMEMORY  400.00                // minimum kB memory to delete saved data file
///#define WHITE_LED 

// sat modem serial port and parameters
#define IRIDIUMSERIAL Serial1            // redefine serial port for sat modem
#define SAT_MODEM_SLEEP 19               // sat modem enable/disable sleep
#define SAT_RXD1 18                      // sat modem serial RXD0 pin, for reference
#define SAT_TXD1 17                      // sat modem serial TXD0 pin, for reference
#define SIZEOFBUFFER 322                 // size of transmit buffer in bytes (max 340)
int signalQuality = -1;                  // set signal quality default
int err = 0;                             // sat modem error number
unsigned int sizeofBuffer;               // size of sat transmit buffer
unsigned int dataSize;                   // size of data in buffer to transmit
uint8_t bufferUp[SIZEOFBUFFER];          // sky transmit buffer for sat modem with high byte and low byte
uint8_t bufferDwn[SIZEOFBUFFER];         // water transmit buffer for sat modem with high byte and low byte

// time 
char daysOfTheWeek[7][12] = {"Sunday", "Monday", "Tuesday", "Wednesday", "Thursday", "Friday", "Saturday"};
String fileDate;                         // create timestamp for file
RTC_DS3231 rtc;                          // declare rtc object
  
// sleep
int wakeup_hr = 11;                      // the time of hour for wakeup
int wakeup_min = 0;                      // the time of minutes for wakeup
bool wakeupType = false;                 // clear wakeup type flag (not RTC wakeup)

// system variables
uint32_t dataUp[SPEC_CHANNELS];          // spectrum Up channel storage array
uint32_t dataDwn[SPEC_CHANNELS];         // spectrum Down channel storage array
const int Averages = 8;                  // number of scans to average, maximum 16
int integrationTimeUp = 0;               // Up sensor integration time in ms
int integrationTimeDwn = 0;              // Down sensor integration time in ms
String wavelengthUp;                     // wavelength of pixel Up channel
String wavelengthDwn;                    // wavelength of pixel Down channel
String up;                               // string to store data to be written to LittleFS
String dwn;                              // string to store data to be written to LittleFS
float AvailLittleFS;                     // amount of LittleFS memory available 
unsigned int dataUpMax;
unsigned int dataDwnMax;
unsigned int AdjintegrationTimeUp;
unsigned int AdjintegrationTimeDwn;
unsigned int scanCount;

// system flags
bool EnableScan = true;                  // set scan enable flag
bool FillTransmitBuffer = false;         // clear fill transmit buffer flag 
bool TransmitData = false;               // clear transmit data flag
bool GotoSleep = false;                  // clear go to deep sleep flag
bool changeIntegrationUp = false;        // clear change integration flag
bool changeIntegrationDwn = false;       // clear change integration flag
bool ManualMode = false;                 // clear manual mode flag to enable sat modem operations

// spectrum data file in LittleSF
const char * SpecDataFile = "/specdata.csv";  // Down sensor calibration coefficients file

// calibration files
const char * pathUp = "/cal_up.csv";      // Up sensor calibration coefficients file
const char * pathDwn = "/cal_down.csv";   // Down sensor calibration coefficients file

// A0cal, B1cal, B2cal, B3cal, B4cal, B5cal, spectrometer wavelength coefficients
double calCoefUp[6];                      // Up sensor calibration coefficients array
double calCoefDwn[6];                     // Down sensor calibration coefficients array

// Declare the IridiumSBD object with SLEEP pin
IridiumSBD modem(IRIDIUMSERIAL, SAT_MODEM_SLEEP);

 
void setup()
{
  Serial.begin(115200);                   // Baud Rate set to 115200
  IRIDIUMSERIAL.begin(19200);             // Start the serial port connected to the satellite modem, default pins
///  Serial1.begin(19200, SERIAL_8N1, SAT_RXD1, SAT_TXD1);  // configure sat modem serial port (does not work)  
///  delay(2000);                              // need delay for serial print statements, debug

  pinMode(UPLOAD_SWITCH, INPUT_PULLUP);   // data upload switch pin with pullup, low for upload
   
  // the alarm wakeup has pullup
  pinMode(WAKEUP_PIN, INPUT_PULLUP);
  
  // wake ESP32 on RTC alarm
  esp_sleep_enable_ext0_wakeup(GPIO_NUM_3,0);  // wake on Low from RTC SQW pin
  
  // configure ADC for Arduino call 
///  analogReadResolution(13);               // valid values 12, 11, 10, 9
///  analogSetAttenuation(ADC_2_5db);        // valid values ADC_0db, ADC_2_5db, ADC_6db, ADC_11db default
///  analogSetClockDiv(1);                   // valid values 1 default (fastest), 255 (slowest)

  // configure ADC with API
  adc1_config_width(ADC_WIDTH_BIT_13);    // requries adc.h

  // Set the ADC Channel gain with API
  adc1_config_channel_atten(ADC1_CHANNEL_0, ADC_ATTEN_DB_2_5);    // requires adc.h, 33us conversion time
  adc1_config_channel_atten(ADC1_CHANNEL_1, ADC_ATTEN_DB_2_5);    // requires adc.h, 33us conversion time

  // initializing the rtc
  if(!rtc.begin()) 
  {
    Serial.println("Couldn't find RTC!");
    Serial.flush();
    while (1) delay(10);
  }

  // this will adjust to the date and time at each compilation, put in once to set clock and then rem out
///     rtc.adjust(DateTime(F(__DATE__), F(__TIME__)));

  // don't need the 32K Pin, so disable it
  rtc.disable32K();
  
  // set alarm 1, 2 flag to false (because alarm 1, 2 didn't happen yet)
  // if not done, this easily leads to problems, as both register aren't reset on reboot/recompile
  rtc.clearAlarm(1);
  rtc.clearAlarm(2);

  // stop oscillating signal at SQW Pin otherwise setAlarm1 will fail
  rtc.writeSqwPinMode(DS3231_OFF);

  // turn off alarm 2 to make sure it is off
  // this isn't done at reboot, so a previously set alarm could easily go overlooked
  rtc.disableAlarm(2);
/*
  // schedule an alarm 30 seconds in the future for testing, this is for debug
  if(!rtc.setAlarm1( rtc.now() + TimeSpan(30),DS3231_A1_Second ))   // this mode triggers the alarm when the seconds match
  {
    Serial.println();
    Serial.println("Error, alarm wasn't set!");
  }
  else 
  {
    Serial.println();
    Serial.println("Alarm will happen in 30 seconds!");
  }
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

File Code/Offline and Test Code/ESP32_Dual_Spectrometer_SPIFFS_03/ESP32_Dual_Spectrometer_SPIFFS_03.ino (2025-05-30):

// Main and Modules are Written by MAS18195
// Spectrometer Test Code that interfaces with Python
// Required Modules:
//	ListFiles.ino
//	PrintSpectrum.ino
//	ReadSpectrum.ino

// This reads the Hammamatsu Spectrometers 288 channels and presents the data to the serial port
// where the host sends request for the X and Y data and an End of Data command when complete
// The host controls how much data is read and it can be less than the 288 channels
// A new scan will not start until the End of Data command is sent

// This has averaging add to the scan channel

// This has LittleSPIFFS to store and retrieve the sensor calibration coefficients
// They are applied to each of the 288 pixel channels

// Two spectrometers have be incorporated

// This adds the ability to adjust the integration time independently for both sensors

// 02/07/2023

// *************** WEMOS PRO PIN OUTS ***************
//    AO            Analog Input, max 3.3V
//    D0   GPIO16  IO, to reset for deep sleep wake, no interrupt or pullup
//    D1   GPIO5   IO, SCL (clock line)
//    D2   GPIO4   IO, SDA (data line)
//    D3   GPIO0   IO, 10k Pull-up
//    D4   GPIO2   IO, 10k Pull-up, Built-in LED
//    D5   GPIO14  IO, SCK (serial clock)
//    D6   GPIO12  IO, MISO (master in slave out)
//    D7   GPIO13  IO, MOSI (master out slave in)
//    D8   GPIO15  IO, 10k Pull-down, SS (slave select)
//----------------------------------------------------------------------------------------


#include <LittleFS.h>
#include <driver/adc.h>
//#include "esp_adc_cal.h"



#define SPEC_ST      9                   // sensor start
#define SPEC_CLK     8                   // sensor clock
// #define SPEC_VIDEO_UP   1                 // ADC1 channel 0
// #define SPEC_VIDEO_DWN  2                 // ADC1 channel 1
///#define WHITE_LED        
#define RELAY       17                    // 5V power enable/disable
#define SPEC_CHANNELS    289              // Spectrum Pixel Channel Bins (288+1 to correct data) 

float wavelengthUp = 0;                   // wavelength of pixel Up channel
float wavelengthDwn = 0;                  // wavelength of pixel Down channel
uint32_t dataUp[SPEC_CHANNELS];           // spectrum Up channel storage array
uint32_t dataDwn[SPEC_CHANNELS];          // spectrum Down channel storage array
bool EnableScan = true;                   // scan enable/disable
int Averages = 8;                         // number of scans to average, maximum 16
int integrationTimeUp = 1;                // Up sensor integration time in ms
int integrationTimeDwn = 2;               // Down sensor integration time in ms
const char * pathUp = "/cal_up.csv";      // Up sensor calibration coefficients file
const char * pathDwn = "/cal_down.csv";    // Down sensor calibration coefficients file

// A0cal, B1cal, B2cal, B3cal, B4cal, B5cal
double calCoefUp[6];                      // Up sensor calibration coefficients array
double calCoefDwn[6];                     // Down sensor calibration coefficients array


void setup()
{
  Serial.begin(115200);                   // Baud Rate set to 115200
////  delay(2000);                            // need delay for serial print statements, debug
  
  // configure ADC for Ardunio call 
///  analogReadResolution(13);               // valid values 12, 11, 10, 9
///  analogSetAttenuation(ADC_2_5db);        // valid values ADC_0db, ADC_2_5db, ADC_6db, ADC_11db default
///  analogSetAttenuation(ADC_0db);
///  analogSetClockDiv(1);                   // valid values 1 default (fastest), 255 (slowest)

  // configure ADC with API
  adc1_config_width(ADC_WIDTH_BIT_13);    // requries adc.h
  adc1_config_channel_atten(ADC1_CHANNEL_0, ADC_ATTEN_DB_2_5);    // requires adc.h
  adc1_config_channel_atten(ADC1_CHANNEL_1, ADC_ATTEN_DB_2_5);    // requires adc.h
  
  // Set desired pins to OUTPUT
  pinMode(SPEC_CLK, OUTPUT);
  pinMode(SPEC_ST, OUTPUT);
  pinMode(RELAY, OUTPUT);
///  pinMode(WHITE_LED, OUTPUT);
  digitalWrite(SPEC_CLK, HIGH);           // Set SPEC_CLK High
  digitalWrite(SPEC_ST, LOW);             // Set SPEC_ST Low
  
  // Mount the file system 
  LittleFS.begin(); 

  // List directory, from root, 2 levels deep
////  Serial.println();                         // debug
////  listDir(LittleFS, "/", 2);                // debug

  // Open Up file for reading
////  Serial.println();                         // debug
////  Serial.printf("Reading file: %s\r\n", path);   // debug
  File file = LittleFS.open(pathUp, "r");

  // Read from file and load calibration coefficient array
////  Serial.println();                         // debug
////  Serial.println("Reading from file:");     // debug
  int j = 0;
  while (file.available()) 
  {
///    Serial.write(file.read());             // send file contents to serial port, debug
    String x = file.readStringUntil(',');     // read and place each coefficient in variable
    calCoefUp[j] = x.toDouble();              // convert string to double float
////    Serial.print(x);  Serial.print("  "); Serial.println(calCoef[j], 20);       // debug
    j += 1;                                   // increment array index
  }
  file.close();
  
  // Open Down file for reading
  ////  Serial.println();                            // debug
////  Serial.printf("Reading file: %s\r\n", path);   // debug
  file = LittleFS.open(pathDwn, "r");
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

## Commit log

2025-05-30 added 3d printed part
    [FOV Adaptor.SLDPRT, FOV Adaptor.STL, RTC Mount.SLDPRT, RTC Mount.STL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]
2025-05-30 added code files
    [04-23-2023.csv, cal_down.csv, cal_up.csv]
2025-05-30 added mech assembly instructions
2025-05-30 added offline support files
    [Example of CoolTerm Output.csv]
2025-05-30 added prototype pictures

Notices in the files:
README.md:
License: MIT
